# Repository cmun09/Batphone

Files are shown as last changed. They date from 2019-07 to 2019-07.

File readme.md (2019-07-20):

# Batphone: Ultrasonic Microphones for Animal Recordings and Research

## Please read through before you go ahead with the microphone. Use it under your own risk. 

I developed this microphone to record ultrasonic soundwaves emitted by bio sonar from bats. 

The quick specifications:

| Specification             | Nominal   | Min                         | Max                         |
| ------------------------- | --------- | --------------------------- | --------------------------- |
| Operating Voltage (V)     | 5         | Minimum of the LDO or opamp | Maximum of the opamp or LDO |
| Frequency Range (Hz)      | 1 - 100K  | 1                           | ∞                           |
| Signal Output Voltage (V) | 0.5 - 3.3 | 0.5                         | 3.3                         |

The microphone itself has very low gain so in order to increase it, you will need to turn the potentiometer.

I have designed in this in EagleCAD. Many different PCB cad software should support or this file type. I believe there ways to export the current file but, I personally do not recommend it. EagleCAD is free with a valid .edu email at Autodesk's website.

Design of the microphone mainly relies on the Knowle's FG sensor. This sensor is rather pricey, going in the ranges for ~$25 USD. The microphones integrity has been tested against a GRAS standard microphone (Unknown model) that displayed a flat frequency response between 1 Hz- 200 kHz with -1db trailing near the end. 
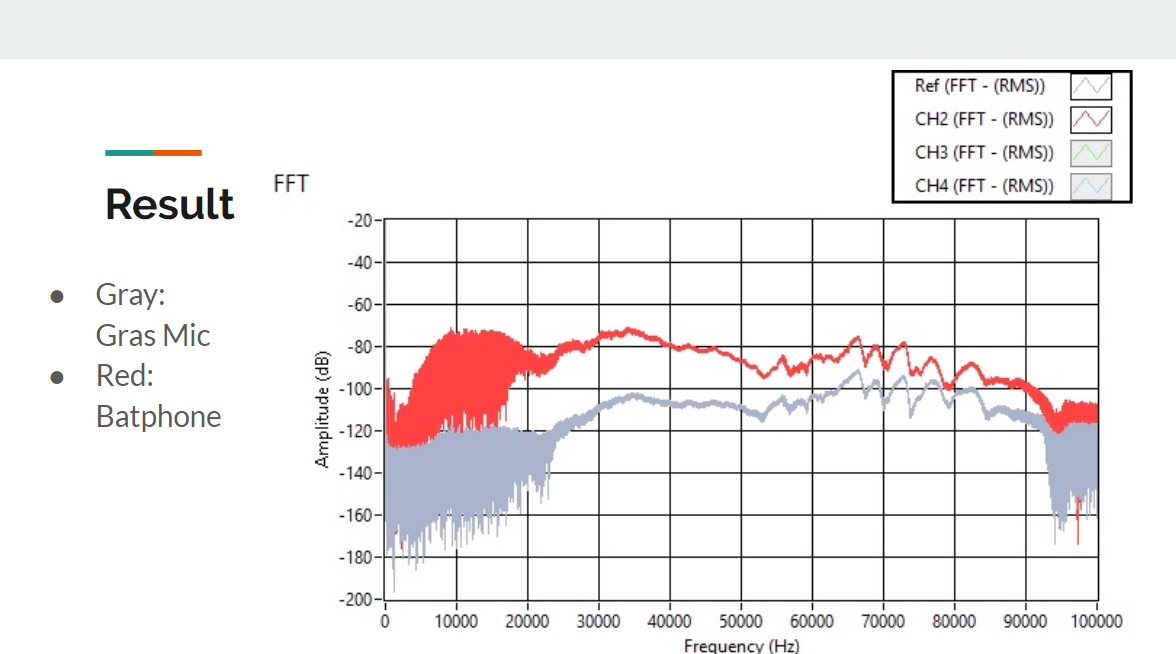
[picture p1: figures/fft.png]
FFT comparison between GRAS and Batphone


My microphone that I have developed is not designed to be used as an replacement microphone for standard microphones but a portable, cheaper, and smaller alternative to the commercial ultrasonic microphones aimed at researches alike.

I thank Dr. Rolf Müeller for overseeing the project and research for his Bat bio-sonar research. 

If you have any questions, please email me at lucasmun@vt.edu.

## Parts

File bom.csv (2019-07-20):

Part | Value | Device | Package | Description | Note | Link | AVAILABILITY | DESCRIPTION | HEIGHT | MANUFACTURER_NAME | MANUFACTURER_PART_NUMBER | MF
C1 | 100pF | C-USC0603 | C0603 | CAPACITOR, American symbol | Low pass | https://www.digikey.com/product-detail/en/walsin-technology-corporation/0603N101F101CT/1292-1472-1-ND/9355476
C2 | 100pF | C-USC0603 | C0603 | CAPACITOR, American symbol | high pass | https://www.digikey.com/product-detail/en/walsin-technology-corporation/0603N101F101CT/1292-1472-1-ND/9355476
C3 | .1uF | C-USC0603 | C0603 | CAPACITOR, American symbol | filter cap for opamp | https://www.digikey.com/product-detail/en/walsin-technology-corporation/0603B104J500CT/1292-1391-1-ND/9355395
C4 | 1uF | C-USC0603 | C0603 | CAPACITOR, American symbol | Filter cap for Regulator | https://www.digikey.com/product-detail/en/samsung-electro-mechanics/CL10A105KA8NNNC/1276-1102-1-ND/3889188
IC1 | MCP6291T-E_OT | MCP6291T-E_OT | SOT95P280X145-5N | Single 10MHz OpAmp,MCP6291T-E/OT | opamp | https://www.digikey.com/product-detail/en/microchip-technology/MCP6291T-E-OT/MCP6291T-E-OTCT-ND/857432 |  | Single 10MHz OpAmp,MCP6291T-E/OT | 1.45mm | Microchip | MCP6291T-E/OT
IC3 | MCP1703CB | MCP1703CB | SOT23 | 250 mA, 16V, Low Quiescent Current LDO Regulator | voltage regulator | https://www.digikey.com/product-detail/en/microchip-technology/MCP1700T-2002E-TT/MCP1700T-2002E-TTCT-ND/8638159
R1 | 10.6k | R-US_R0603 | R0603 | RESISTOR, American symbol | low pass | https://www.digikey.com/product-detail/en/stackpole-electronics-inc/RMCF0603FT10K5/RMCF0603FT10K5CT-ND/1943059
R2 | 80k | R-US_R0603 | R0603 | RESISTOR, American symbol | high pass | https://www.digikey.com/product-detail/en/yageo/RC0603FR-0780K6L/311-80.6KHRCT-ND/730343
R3 | 2k | R-US_R0603 | R0603 | RESISTOR, American symbol | r_i | https://www.digikey.com/product-detail/en/yageo/RC0603FR-072KL/311-2.00KHRCT-ND/729956
R6 | TC33X-2-103E | TC33X-2-103E | 35WR | http://octopart.com/tc33x-2-103e-bourns-68150 | r_f | https://www.digikey.com/product-detail/en/bourns-inc/TC33X-2-104E/TC33X-104EDKR-ND/1785032 | Unavailable | Res Trimmer 10K Ohm 25% 0.1W_1/10W_ 1_Elec_/1_Mech_Turn _3 X 3.8mm_ Foot Print SMD Embossed T/R |  |  |  | Bourns
SV1 | 4 pos | MA04-1 | MA04-1 | PIN HEADER | regular 2.54mm pin header

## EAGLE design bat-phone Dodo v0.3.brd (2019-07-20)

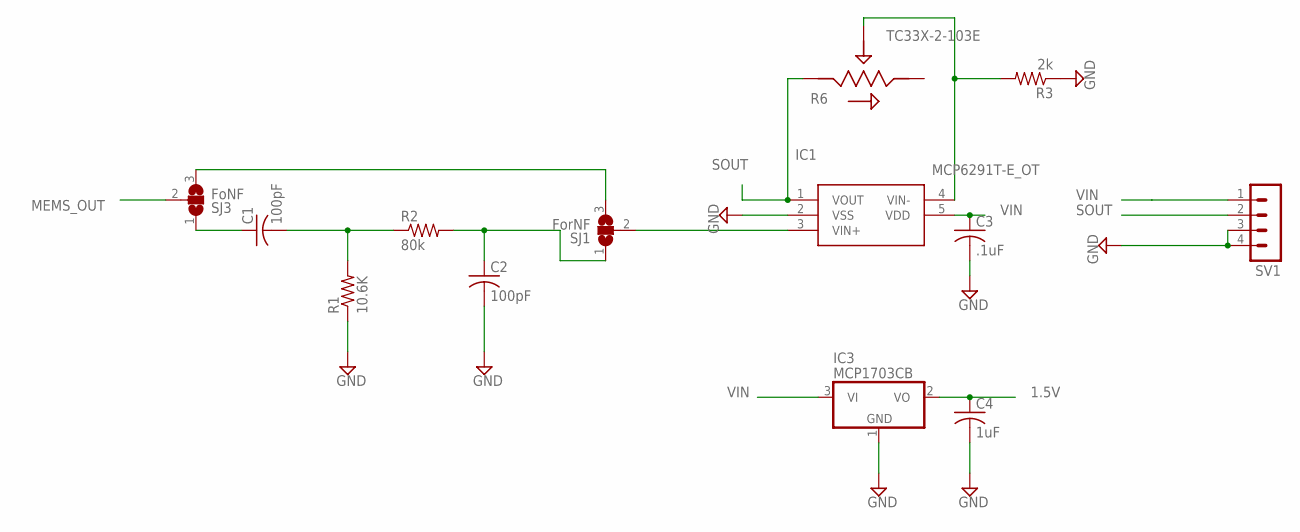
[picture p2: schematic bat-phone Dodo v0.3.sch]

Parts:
C1, C2: 100pF; C0603
C3: .1uF; C0603
C4: 1uF; C0603
IC1: MCP6291T-E_OT; SOT95P280X145-5N
IC3: MCP1703CB; SOT23
R1: 10.6K; R0603
R2: 80k; R0603
R3: 2k; R0603
R6: TC33X-2-103E; 35WR
SJ1: ForNF; SJ_2
SJ3: FoNF; SJ_2
SV1: MA04-1

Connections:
1.5V: C4.1, IC3.2 (VO)
GND: C2.2, C3.2, C4.2, IC1.2 (VSS), IC3.1 (GND), R1.1, R3.1, SV1.3, SV1.4
MEMS_OUT: SJ3.2
unnamed: IC1.3 (VIN+), SJ1.2
unnamed: C1.2, R1.2, R2.1
unnamed: C2.1, R2.2, SJ1.1
unnamed: IC1.4 (VIN-), R3.2, R6.2
unnamed: SJ1.3, SJ3.3
unnamed: C1.1, SJ3.1
SOUT: IC1.1 (VOUT), R6.1, SV1.2
VIN: C3.1, IC1.5 (VDD), IC3.3 (VI), SV1.1

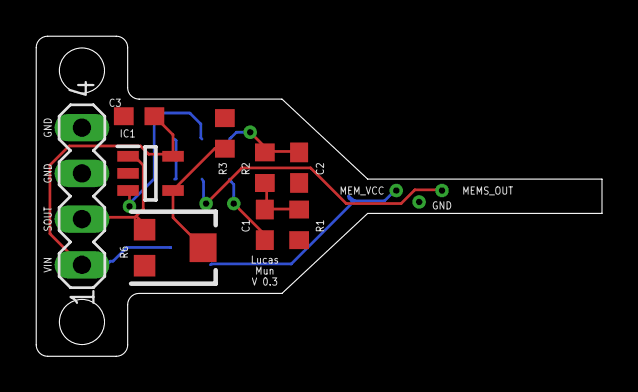
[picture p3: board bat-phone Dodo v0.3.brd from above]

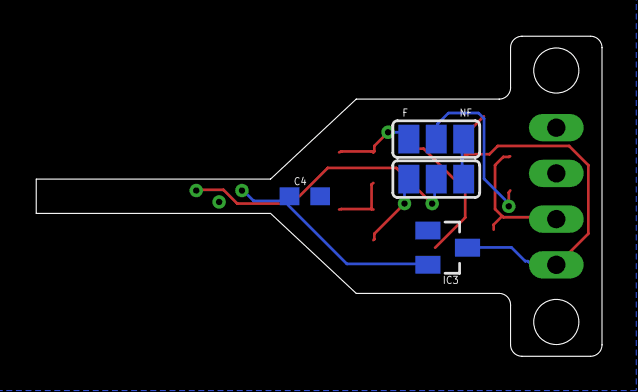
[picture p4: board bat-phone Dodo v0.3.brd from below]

Board: 2 copper layers, 31.4 x 17.8 mm, 13 parts (4 on the bottom side), 10 nets.

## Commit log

2019-07-20 Inital Files
    [bat-phone Dodo v0.3.brd, bat-phone Dodo v0.3.sch, bom.csv]
2019-07-20 Updated BOM
    [bom.csv]
